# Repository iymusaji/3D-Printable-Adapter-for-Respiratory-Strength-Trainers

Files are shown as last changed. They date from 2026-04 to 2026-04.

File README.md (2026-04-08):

# 3D-Printable-Adapter-for-Respiratory-Strength-Trainers

A simple 3D-printed adapter designed to attach to a hands-free harmonica holder so round therapy devices, such as EMST and IMST trainers, can be positioned in front of a client’s mouth during therapy tasks.
person wearing device

This project was developed to improve access for individuals with mobility, motor, or strength impairments, including stroke survivors and people with progressive, degenerative, neurological, or other complex motor conditions.

---
## 3D Model Images
3d adapter 1
3D adapter 2

---
## Project Summary

This project developed a simple, practical 3d-printable adapter for use with hands-free harmonica mounts.

The adapter allows round respiratory therapy devices, such as **EMST** and **IMST** trainers, to be held in place without requiring the client to independently position or support the device. This can make therapy tasks more accessible for individuals with physical impairments that affect upper extremity use, posture, endurance, coordination, or strength.

The inventor (Olivia Kerr) printed the prototype and piloted it with clients through local community partner organizations.

The design is being shared so that speech-language pathologists, respiratory therapists, and other clinicians or support teams can print and adapt similar tools for [**noncommercial use**](https://creativecommons.org/licenses/by-nc-sa/4.0/), provided attribution is given and any adaptations are shared under the same license.

---

## Why This Matters

Many clients who benefit from expiratory or inspiratory muscle strength training may also have difficulty holding or positioning therapy equipment consistently and safely. A mountable adapter can help:

- improve access to therapy tasks
- reduce the need for manual assistance
- support more consistent device positioning
- increase independence for some users
- reduce setup burden for clinicians and caregivers

---

## Intended Users

This project may be useful for:

- speech-language pathologists (SLPs)
- respiratory therapists (RTs)
- occupational therapists and rehabilitation teams
- caregivers and support personnel
- makers and clinicians supporting adaptive access solutions

---

## Acknowledgments

This project was innovated, developed, and tested by **Olivia Kerr**, speech-language pathology graduate clinician.

The project was completed with supervision from **Imran Musaji, PhD, CCC-SLP**, Assistant Professor in the Department of Communication Sciences and Disorders at Wichita State University, and with design and 3D-modeling collaboration from **Paul Herring**, Professor in Plastics Engineering Technology at Pittsburg State University.

The prototype was piloted through local community partner organizations including the Wichita State University Evelyn Hendren Cassat Speech-Language Pathology Clinica and the Speech Swallowing Voice Center.

Special thanks to the clinicians, clients, and community partners who supported early testing and feedback.

If citing this work for academic or creative commons license purposes, use the following attribution.

Suggestions, improvements, and noncommercial adaptations are welcome. If you modify this design, please provide attribution and share your adapted version under the same license terms.

---

## Suggested Citation

Kerr, O., Herring, P., & Musaji, I. (2026). *Hands-free 3D-Printable Harmonica-Mount Adapter for Respiratory-Strength-Trainers* [3D design files and project documentation]. GitHub. https://github.com/iymusaji/3D-Printable-Adapter-for-Respiratory-Strength-Trainers

---

## What This Repository Includes

This repository is intended to share:

- the 3D printable adapter parts (top and bottom)
  -EMSTL2.STL
  -EMSTU2.STL
- instructions for modifying a harmonica holder
- A video showing assembly with a sample EMST device installed
- information about materials and assembly
- licensing details for reuse and adaptation

---

## Usage Notes

This adapter was designed to support round therapy devices such as EMST and IMST trainers by mounting them to a hands-free holder.

Because therapy devices, holder styles, and client needs can vary, users should review fit, positioning, and tolerance before clinical use. Adjustments may be needed for different hardware or patient presentations.

**_Safety and Clinical Disclaimer_
**
This project is a prototype adaptation intended to support accessibility and clinical creativity. It is not a regulated medical device and has not been formally tested for universal clinical use.

Users are responsible for:

evaluating safety and suitability for their setting
confirming secure assembly before each use
using clinical judgment when introducing the device in therapy
monitoring client comfort, positioning, and tolerance

Do not use a damaged, unstable, or poorly fitted setup.

---

## License

This project is licensed under the Creative Commons Attribution-NonCommercial-ShareAlike 4.0 International License (CC BY-NC-SA 4.0).

Under this license, others may:

share the material
remix, adapt, and build upon it

Under the following conditions:

Attribution — credit must be given to the original creator
NonCommercial — use must be noncommercial
ShareAlike — adaptations must be distributed under the same license

For the full license text, see:
[CC BY-NC-SA 4.0](https://creativecommons.org/licenses/by-nc-sa/4.0/)

---

## Materials Needed

### Required
- Hands-free harmonica holder
-   There are many models available. We used "OriGlam Harmonica Holder Neck Holder Stand, Mouth Organ Metal Frame Adjustable for 10 Hole Harmonica" for $8.98 off Amazon
- Wire cutters or jewelry cutters
- Super glue

### 3D Printing Note
- 3D printed adapter components (the prototype was printed on an Ender -3 V2)
-   The adapter was printed using standard PLA polymer fillament.
-   Build time for both parts was less than 45 minutes.
 3D Software

### Adhesives Used in This Prototype
- **J-B Weld SuperWeld Instant Adhesive** — approximately $5.97 at Walmart
- **Loctite Super Glue Liquid Brush On** — approximately $4.77 at Walmart

### Optional
- Sandpaper  
  Useful for lightly sanding surfaces before gluing to improve adhesion.

---

## Harmonica Holder Modification Instructions

These are the steps that worked for this prototype. You may need to adjust measurements slightly depending on the specific harmonica holder used.

adapter1

Adapter2

### 3. Trim the springs
Use wire cutters to remove approximately **3/4 inch** from the springs.

This reduces resistance and made the holder easier to use in this build.

- Remove more or less as needed for your setup.
- The measurement above is simply what worked for me.

Adapter3

### 4. Optional surface prep
Optionally sand:

- the bottom of the 3D printed support bracket
- the metal area of the harmonica holder where the bracket will be attached

This may improve glue adhesion.

### 5. Attach the bottom support bracket
Glue the bottom 3D printed support bracket onto the harmonica holder.

### 6. Attach the top bracket
Pop the top 3D printed bracket onto the top bar.

### 7. Check final fit
Before use, confirm that:

- the adapter is firmly attached
- the mounted device sits in the intended position
- the setup is stable during therapy tasks

Final

Infill: 20%
Supports: As needed depending on orientation

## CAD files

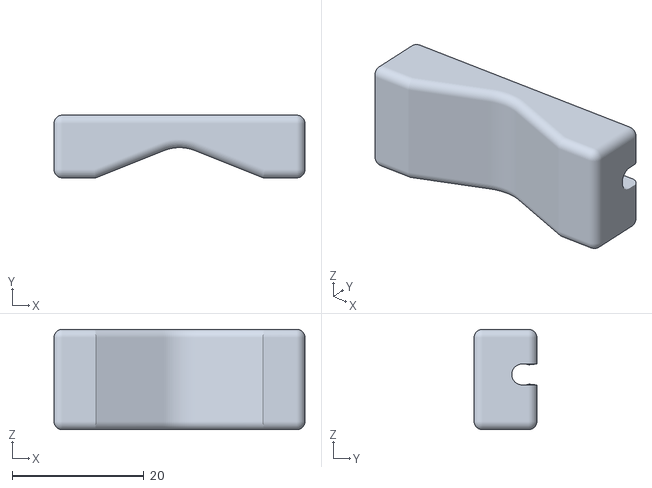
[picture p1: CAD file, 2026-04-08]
EMSTU2.STL
38.1 x 9.53 x 15.2

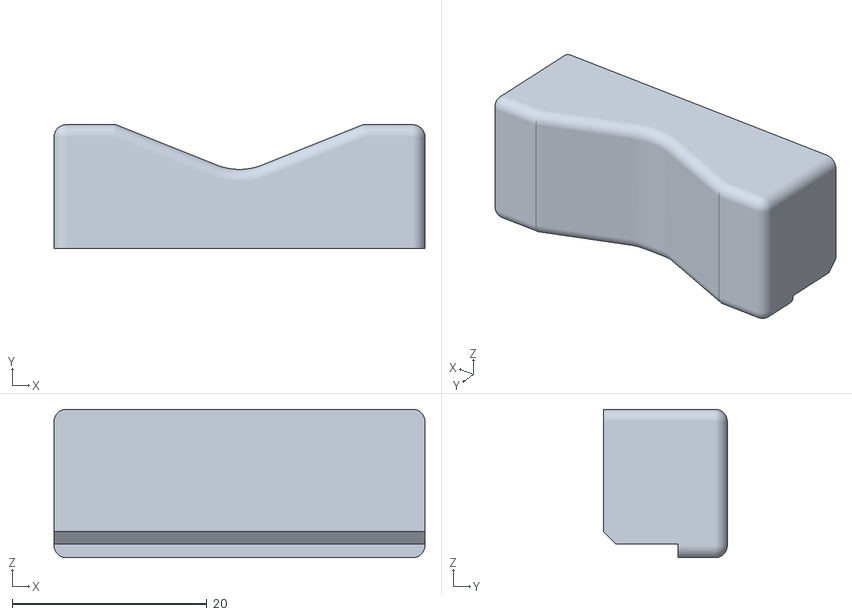
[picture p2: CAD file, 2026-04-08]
EMSTL2.STL
38.1 x 12.7 x 15.2
